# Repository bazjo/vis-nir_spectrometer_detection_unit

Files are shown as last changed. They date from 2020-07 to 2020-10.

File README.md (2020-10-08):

# vis-nir_spectrometer_detection_unit
This project contains a high-resolution detection unit for VIS/NIR spectroscopy using the Hamamatsu S1337-1010 photodiode and the Analog AD7768-1 24 Bit ADC.

It was developed as a student project in the summer term of 2020 in the course "Optical Spectroscopy and its Applications" at Cologne University of Applied Sciences.

## Getting Started

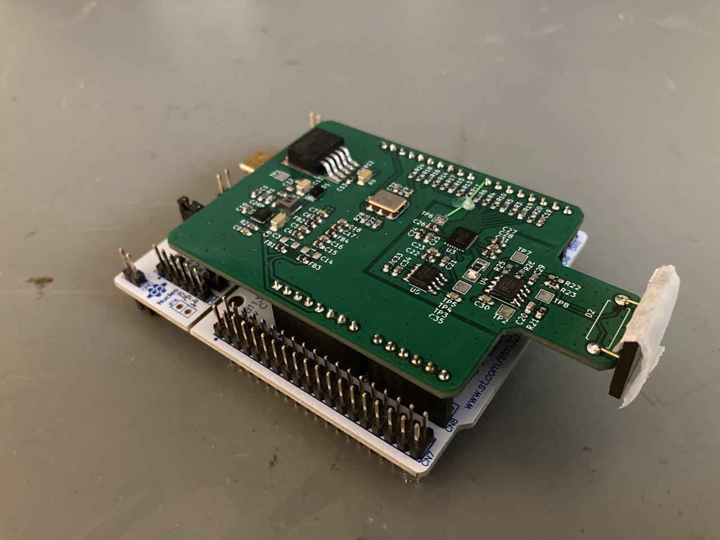
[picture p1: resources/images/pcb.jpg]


The PCB is designed to utilize an Arduino shield footprint for use with various breakout boards, such as ST Nucleo STM32 development boards or the avnet MiniZed development platform for Xilinx Zynq.

It features power filtering and an -5V inverter, the AD7768-1 DC to 204 kHz 24-Bit ADC (connected via SPI) with a 4.096 V ADR4540 and a photodiode front end featuring the AD8622 OpAmp. When a tunable clock is not available, i.e. when no FPGA is used, the main clock can be provided by an Si514 Any Frequency Programmable Oscillator (connected via I2C).

The photodiode is attached at the front to be mounted inside the spectrometer.

When assembling the PCB please look out for the bodges/errata. The PCB has been designed using kicad.

Demo applications are provided for the Arduino platform (just for the Si514 as the AD7768-1 requires 16-Bit SPI which is not yet supported by Arduino) and the STM32 platform. This application is designed for the Nucleo F401RE and was developed using the Crossley CrossWorks for ARM IDE. The code can be compiled with the trial version. This demo Application continuously sends data to a connected computer at 300 Sp/s via a serial connection.

## Theory of Operation

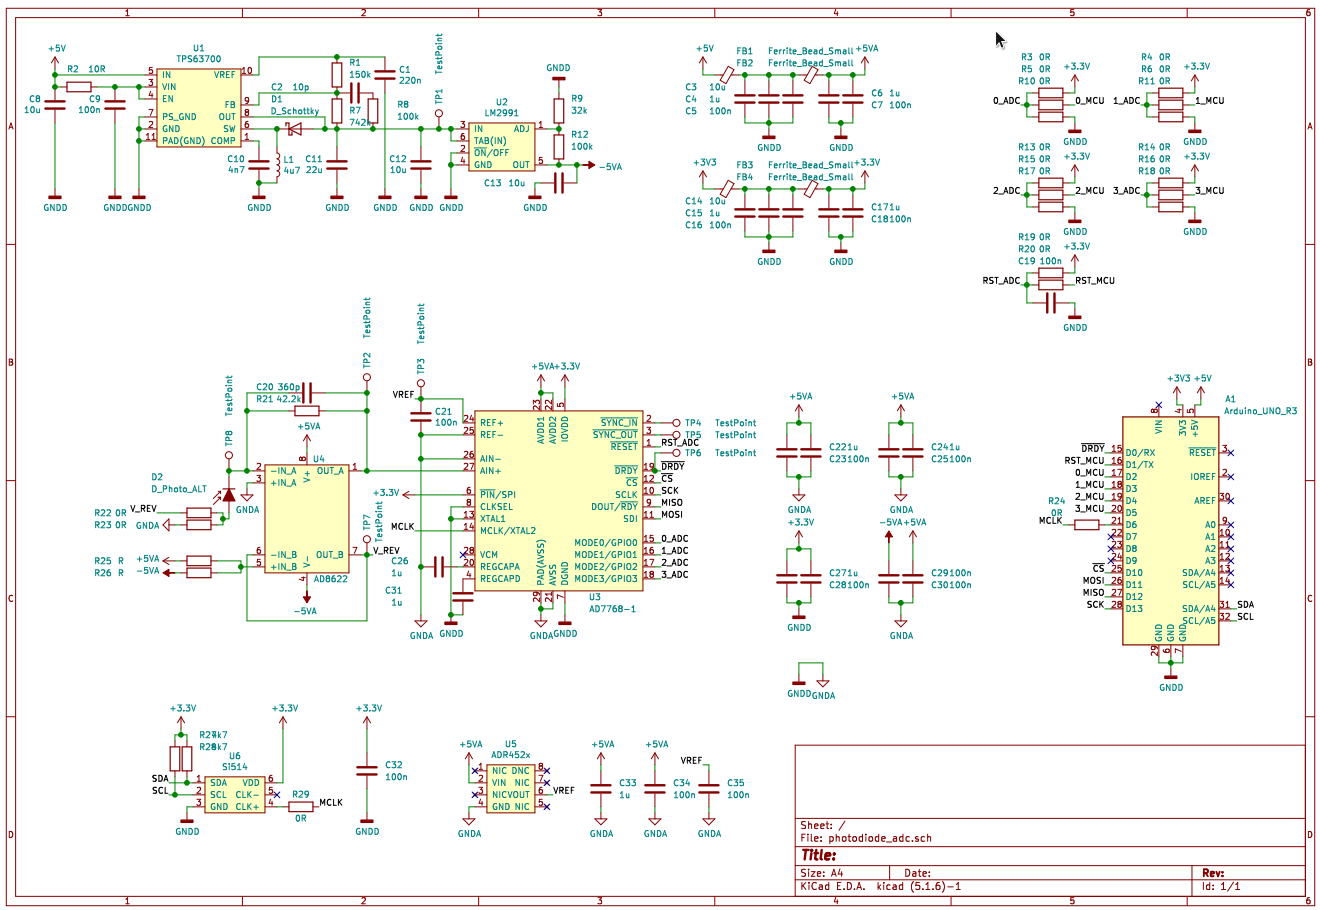
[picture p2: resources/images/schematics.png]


### Pinout
[jumpered] Pins must be connected by a designated jumper resistor.

Arduino Pin | STM32F401RE Pin | Connection
---|---|---
D0|PA3|none (!DRDY if not bodged)
D1|PA2|[jumpered] AD7768-1 !RESET
D2|PA10|[jumpered] AD7768-1 GPIO0
D3|PB3|[jumpered] AD7768-1 GPIO1
D4|PB5|[jumpered] AD7768-1 GPIO2
D5|PB4|[jumpered] AD7768-1 GPIO3
D6|PB10|[jumpered] AD7768-1 MCLK
D7|PA8|AD7768-1 !DRDY after bodge
D10|PB6|AD7768-1 !CS
D11|PA7|AD7768-1 MOSI
D12|PA6|AD7768-1 MISO
D13|PA5|AD7768-1 SCK
SDA|PB9|Si514 SDA
SCL|PB8|Si514 SCL

### Bodges/Errata
There are two problems with the pcb which are minor enough not to roll out a new revision
1. The Arduino RX/TX pins are used for GPIO. Unfortunately those Pins are used for the VCP connection on the Nucleo boards as well. The needed connection !DRDY is therefore rerouted to pin D7. This bodge can be performed by drilling the via on !DRDY with 0.8 mm drill bit and soldering a bodge wire between TP6 and D7.
2. When using the ADC on it's own, sync pulses can be generated via SPI. Those need to be send from SYNC_OUT to SYNC_IN. For this, bridge TP4 and TP5 with a 1206 0R resistor.

### PSU
The circuit uses three voltage rails. The 3V3 and 5V rails are used straight from the baseboard and are filtered through a 2-Stage LC PI-filter. The -5V rail is generated locally with TPS63700 inverter and subsequent LM2991 LDO. Power Planes are located on the second inner layer of the PCB. there are different planes for analog and digital ground, whose domains are joint below the high-speed adc interface to prevent loop currents.

### Oscillator
The Si514 Oscillator is attached via I2C and is equipped with pullup resistors. The source for the ADC MCLK can be selected between Si514 and baseboard via means of the resistor jumpers R24/R29. The tap R29 could also be used for MCLK monitoring.

### ADC + Frontend
The AD7768 was chosen for a few different reasons. First of all, it is a 24-Bit ADC suitable for low frequencies and even DC. Further, it features digital signal processing capabilities difficult to implement in a MCU. Most importantly, it allows for a wide range of decimation rates and a highly customizable sample rate so that acquisitions can be matched to the speed of a wavelength selective element. The ADC is connected via SPI. It is used in a pseudo-differential configuration with a 4.096 V reference ADR4540, to measure a voltage range between 0 an 4.096 V. The lowest possible sample rate with the highest decimation of 1024x is 300 Sp/s.

The ADC is paired with a transimpedance photodiode amplifier which is realized upon 1/2 of an AD8622 OpAmp. The values of the feedback network are matched in accordance to the photodiode sensitivity and speed. The photodiodes anode can be connected to ground via R23 or the diode can be reversed biased via R22. Reverse bias is generated through the other 1/2 of the AD8622 buffering an voltage divider R25/R26.

The photodiode is a Hamamatsu S1337-1010. It's spectral response from 190/340-1100 nm enables its use in VIS and certain NIR applications. The large area guarantees a high photosensitivity, and the rise time is fast enough for the desired spectroscopy application.

## Software Examples
The included software provides functions to interface with the hardware on the PCB.

The function `Set_Si514_Frequency()` configures the Si514 and has to be executed after every restart. It expects an array of register values which can be calculated through the Silab Utility provided in /resources/tools.

The functions to read an write from/to the AD7768-1 registers in general feature 8 bit wide addresses and values. An exemption is the result register, which is 24 bit wide an therefore is internally handled as an uint32.

After the ICs are configured, a SYNC pulse is triggered which starts the continuous adc capture. Every time a new sample is ready, a falling edge is presented to the MCU by the adc on !DRDY which is captured through an interrupt, and sets a flag, which enables a readout in the main program loop. Depending upon configuration of the variable `average_mode`, the result is either output through a serial connection right away, or after 256 samples have been averaged.

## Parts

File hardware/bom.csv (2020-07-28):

Reference | Quantity | Value | Footprint | Datasheet
A1 | 1 | Arduino_UNO_R3 | Module:Arduino_UNO_R3 | https://www.arduino.cc/en/Main/arduinoBoardUno
C1 | 1 | 220n | Capacitor_SMD:C_0603_1608Metric_Pad1.05x0.95mm_HandSolder | ~
C10 | 1 | 4n7 | Capacitor_SMD:C_0603_1608Metric_Pad1.05x0.95mm_HandSolder | ~
C11 | 1 | 22u | Capacitor_SMD:C_1206_3216Metric_Pad1.42x1.75mm_HandSolder | ~
C2 | 1 | 10p | Capacitor_SMD:C_0603_1608Metric_Pad1.05x0.95mm_HandSolder | ~
C20 | 1 | 360p | Capacitor_SMD:C_0603_1608Metric_Pad1.05x0.95mm_HandSolder | ~
C21 C19 C5 C7 C16 C18 C9 C32 C34 C35 C23 C25 C28 C29 C30 | 15 | 100n | Capacitor_SMD:C_0603_1608Metric_Pad1.05x0.95mm_HandSolder | ~
C3 C14 C8 C12 C13 | 5 | 10u | Capacitor_SMD:C_1206_3216Metric_Pad1.42x1.75mm_HandSolder | ~
C4 C6 C15 C17 C33 C26 C31 C22 C24 C27 | 10 | 1u | Capacitor_SMD:C_0603_1608Metric_Pad1.05x0.95mm_HandSolder | ~
D1 | 1 | D_Schottky | Diode_SMD:D_SMF | ~
D2 | 1 | D_Photo_ALT | Resistor_THT:R_Axial_Power_L48.0mm_W12.5mm_P7.62mm_Vertical | ~
FB1 FB2 FB3 FB4 | 4 | Ferrite_Bead_Small | Capacitor_SMD:C_0603_1608Metric_Pad1.05x0.95mm_HandSolder | ~
L1 | 1 | 4u7 | Inductor_SMD:L_Wuerth_MAPI-3020 | ~
R1 | 1 | 150k | Resistor_SMD:R_0603_1608Metric_Pad1.05x0.95mm_HandSolder | ~
R2 | 1 | 10R | Resistor_SMD:R_0603_1608Metric_Pad1.05x0.95mm_HandSolder | ~
R21 | 1 | 42.2k | Resistor_SMD:R_0603_1608Metric_Pad1.05x0.95mm_HandSolder | ~
R25 R26 | 2 | R | Resistor_SMD:R_0603_1608Metric_Pad1.05x0.95mm_HandSolder | ~
R28 R27 | 2 | 4k7 | Resistor_SMD:R_0603_1608Metric_Pad1.05x0.95mm_HandSolder | ~
R4 R6 R11 R14 R16 R18 R13 R15 R17 R3 R5 R10 R19 R20 R24 R22 R23 R29 | 18 | 0R | Resistor_SMD:R_0603_1608Metric_Pad1.05x0.95mm_HandSolder | ~
R7 | 1 | 742k | Resistor_SMD:R_0603_1608Metric_Pad1.05x0.95mm_HandSolder | ~
R8 R12 | 2 | 100k | Resistor_SMD:R_0603_1608Metric_Pad1.05x0.95mm_HandSolder | ~
R9 | 1 | 32k | Resistor_SMD:R_0603_1608Metric_Pad1.05x0.95mm_HandSolder | ~
TP4 TP5 TP6 TP2 TP3 TP7 TP1 TP8 | 8 | TestPoint | TestPoint:TestPoint_Pad_2.0x2.0mm | ~
U1 | 1 | TPS63700 | Package_SON:VSON-10-1EP_3x3mm_P0.5mm_EP1.65x2.4mm_ThermalVias
U2 | 1 | LM2991 | Package_TO_SOT_SMD:TO-263-5_TabPin6
U3 | 1 | AD7768-1 | Package_DFN_QFN:QFN-28-1EP_4x5mm_P0.5mm_EP2.65x3.65mm_ThermalVias
U4 | 1 | AD8622 | Package_SO:SOIC-8_3.9x4.9mm_P1.27mm
U5 | 1 | ADR452x | Package_SO:SOIC-8_3.9x4.9mm_P1.27mm
U6 | 1 | Si514 | Oscillator:Oscillator_SMD_IDT_JU6-6_7.0x5.0mm_P2.54mm

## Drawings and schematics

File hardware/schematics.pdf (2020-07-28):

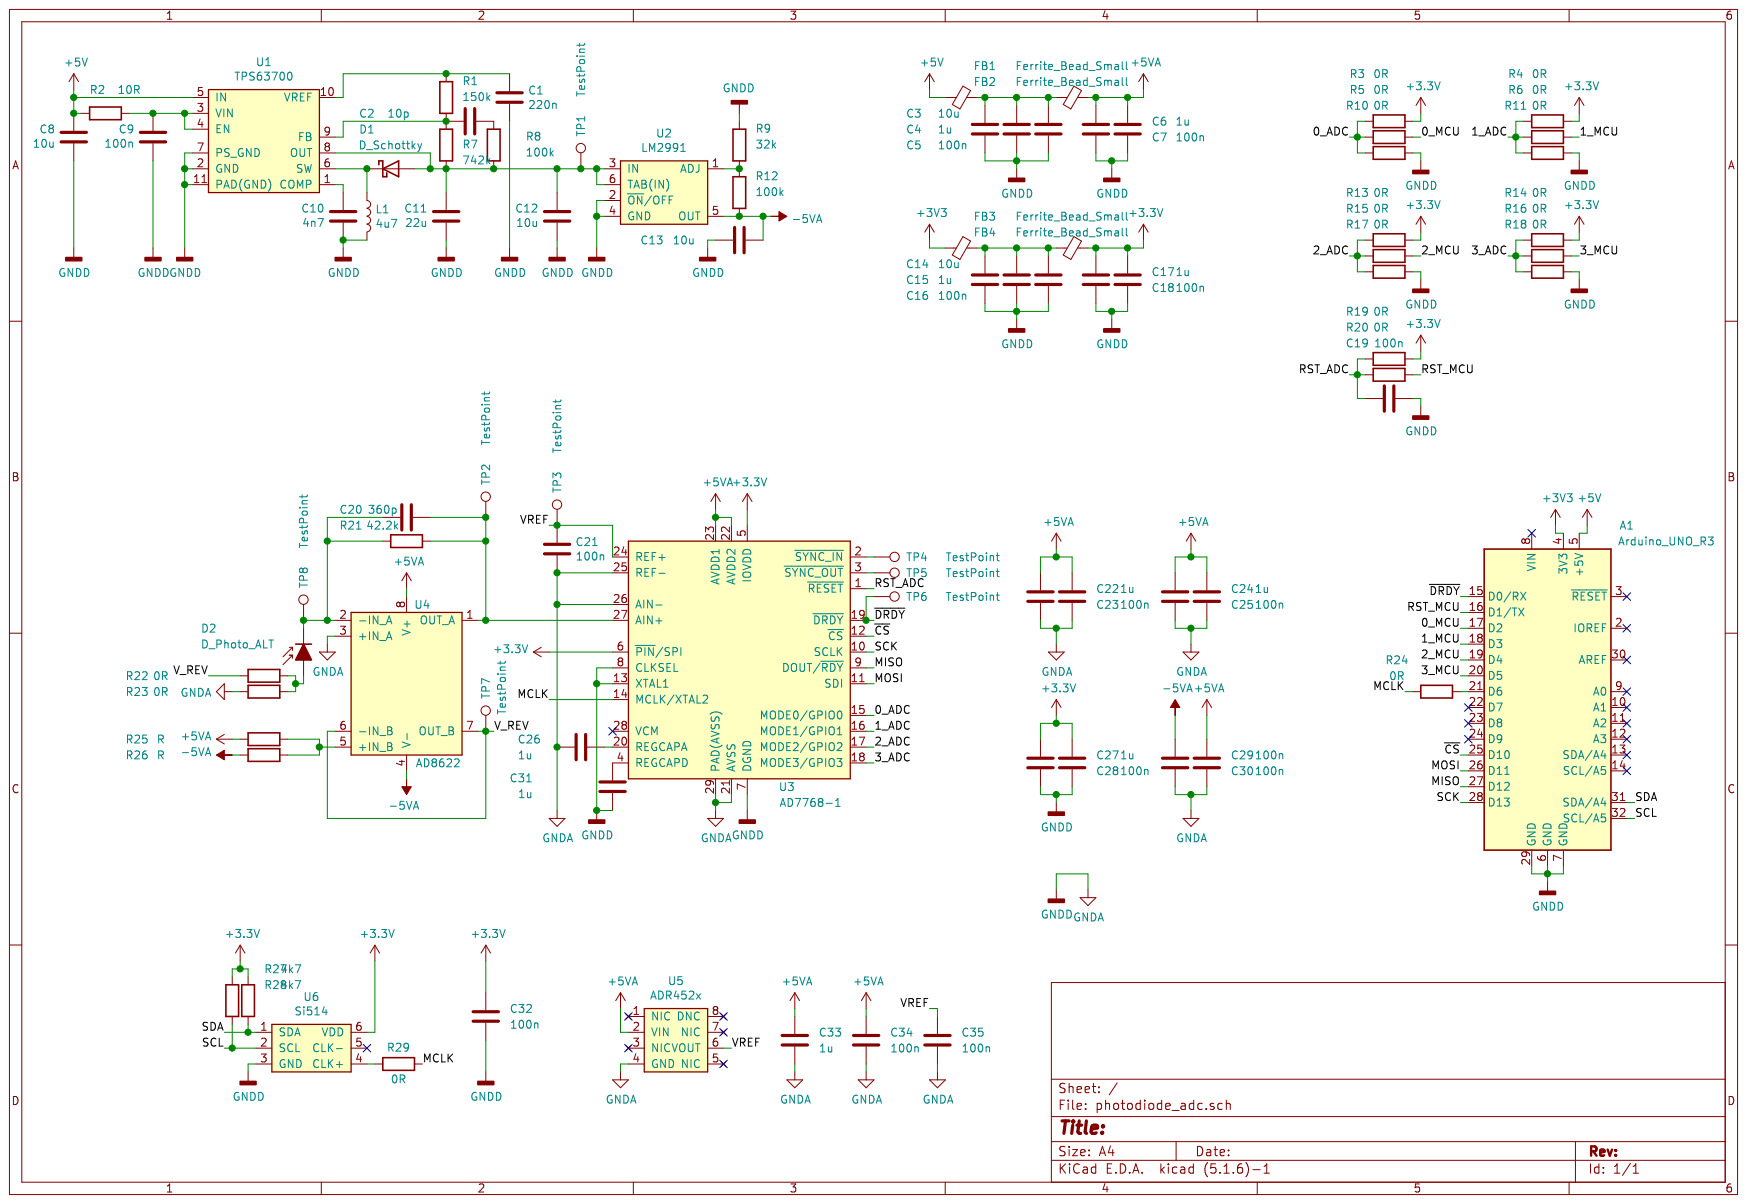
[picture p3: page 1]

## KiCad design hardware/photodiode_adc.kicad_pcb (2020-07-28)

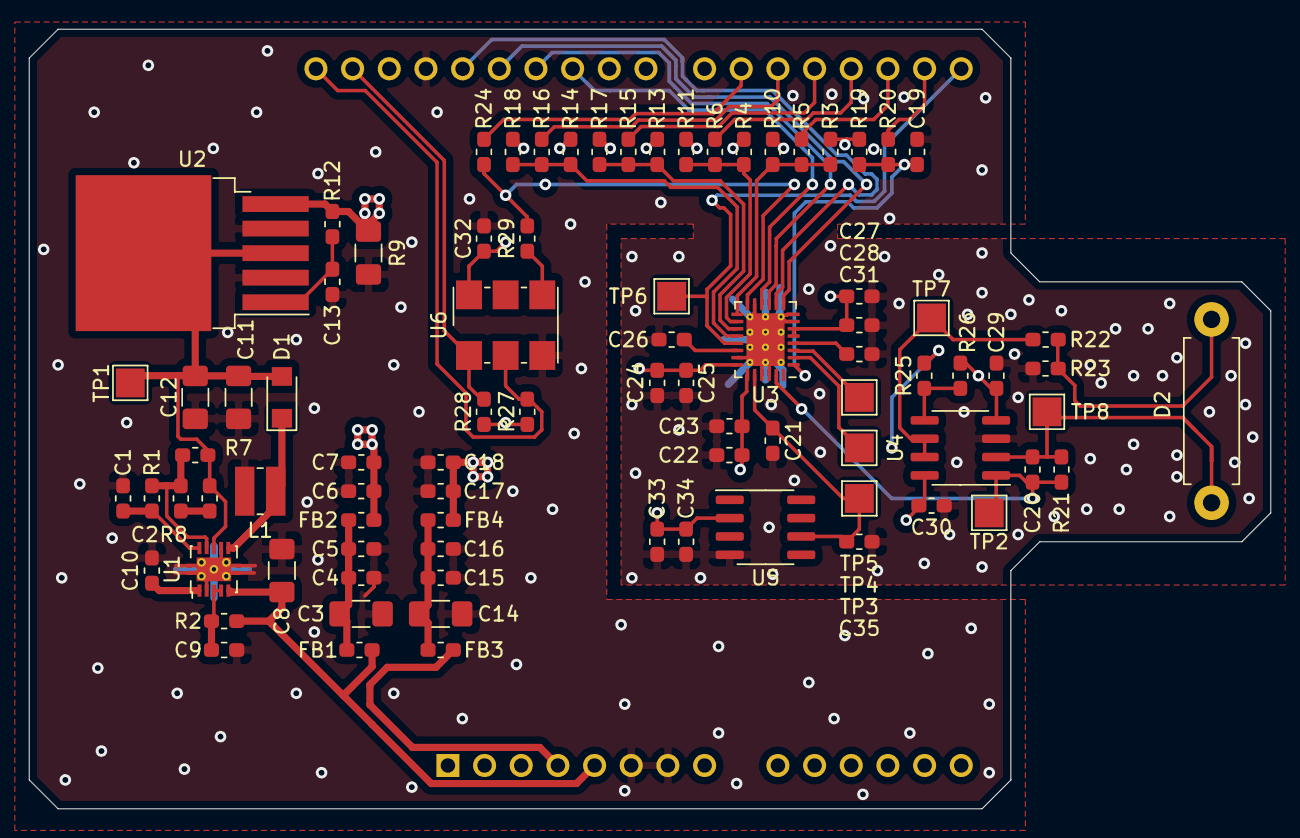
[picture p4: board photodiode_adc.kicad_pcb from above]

Board: 4 copper layers, 86.0 x 54.0 mm, 86 parts (1 on the bottom side), 45 nets.

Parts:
A1: Arduino_UNO_R3; Arduino_UNO_R3_NoSilk
C1: 220n; C_0603_1608Metric_Pad1.05x0.95mm_HandSolder
C2: 10p; C_0603_1608Metric_Pad1.05x0.95mm_HandSolder
C3, C8, C12, C13, C14: 10u; C_1206_3216Metric_Pad1.42x1.75mm_HandSolder
C4, C6, C15, C17, C22, C24, C26, C27, C31, C33: 1u; C_0603_1608Metric_Pad1.05x0.95mm_HandSolder
C5, C7, C9, C16, C18, C19, C21, C23, C25, C28, C29, C30, C32, C34, C35: 100n; C_0603_1608Metric_Pad1.05x0.95mm_HandSolder
C10: 4n7; C_0603_1608Metric_Pad1.05x0.95mm_HandSolder
C11: 22u; C_1206_3216Metric_Pad1.42x1.75mm_HandSolder
C20: 360p; C_0603_1608Metric_Pad1.05x0.95mm_HandSolder
D1: D_Schottky; D_SMF
D2: D_Photo_ALT; R_Axial_DIN0411_L9.9mm_D3.6mm_P12.70mm_Horizontal
FB1, FB2, FB3, FB4: Ferrite_Bead_Small; C_0603_1608Metric_Pad1.05x0.95mm_HandSolder
L1: 4u7; L_Wuerth_MAPI-3020
R1: 150k; R_0603_1608Metric_Pad1.05x0.95mm_HandSolder
R2: 10R; R_0603_1608Metric_Pad1.05x0.95mm_HandSolder
R3, R4, R5, R6, R10, R11, R13, R14, R15, R16, R17, R18, R19, R20, R22, R23, R24, R29: 0R; R_0603_1608Metric_Pad1.05x0.95mm_HandSolder
R7: 742k; R_0603_1608Metric_Pad1.05x0.95mm_HandSolder
R8, R12: 100k; R_0603_1608Metric_Pad1.05x0.95mm_HandSolder
R9: 32k; R_0603_1608Metric_Pad1.05x0.95mm_HandSolder
R21: 42.2k; R_0603_1608Metric_Pad1.05x0.95mm_HandSolder
R25, R26: R; R_0603_1608Metric_Pad1.05x0.95mm_HandSolder
R27, R28: 4k7; R_0603_1608Metric_Pad1.05x0.95mm_HandSolder
TP1, TP2, TP3, TP4, TP5, TP6, TP7, TP8: TestPoint; TestPoint_Pad_2.0x2.0mm
U1: TPS63700; VSON-10-1EP_3x3mm_P0.5mm_EP1.65x2.4mm_ThermalVias
U2: LM2991; TO-263-5_TabPin6
U3: AD7768-1; QFN-28-1EP_4x5mm_P0.5mm_EP2.65x3.65mm_ThermalVias
U4: AD8622; SOIC-8_3.9x4.9mm_P1.27mm
U5: ADR452x; SOIC-8_3.9x4.9mm_P1.27mm
U6: Si514; Oscillator_SMD_IDT_JU6-6_7.0x5.0mm_P2.54mm

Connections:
+3V3: A1.4, C17.1, C18.1, C27.1, C28.1, C32.1, FB3.2, FB4.1, R3.1, R4.1, R13.1, R14.1, R19.1, R27.1, R28.1, U3.5, U3.6, U6.6
+5V: A1.5, C8.2, FB1.2, R2.2, U1.5
+5VA: C6.1, C7.1, C22.1, C23.1, C24.1, C25.1, C30.1, C33.1, C34.1, FB2.1, R25.2, U3.22, U3.23, U4.8, U5.2
-5VA: C13.2, C29.1, R12.1, R26.2, U2.5, U4.4
/0_ADC: R3.2, R5.2, R10.2, U3.15
/0_MCU: A1.17, R5.1
/1_ADC: R4.2, R6.2, R11.2, U3.16
/1_MCU: A1.18, R6.1
/2_ADC: R13.2, R15.2, R17.2, U3.17
/2_MCU: A1.19, R15.1
/3_ADC: R14.2, R16.2, R18.2, U3.18
/3_MCU: A1.20, R16.1
/MCLK: R24.2, R29.2, U3.14
/MISO: A1.27, U3.9
/MOSI: A1.26, U3.11
/RST_ADC: C19.2, R19.2, R20.2, U3.1
/RST_MCU: A1.16, R20.1
/SCK: A1.28, U3.10
/SCL: A1.32, R27.2, U6.2
/SDA: A1.31, R28.2, U6.1
/VREF: C21.1, C35.1, TP3.1, U3.24, U5.6
/V_REV: R22.2, TP7.1, U4.6, U4.7
/~CS~: A1.25, U3.12
/~DRDY~: A1.15, TP6.1, U3.19
GNDA: A1.6, A1.7, A1.29, C1.2, C3.2, C4.2, C5.2, C6.2, C7.2, C8.1, C9.1, C10.1, C11.1, C12.1, C13.1, C14.2, C15.2, C16.2, C17.2, C18.2, C19.1, C21.2, C22.2, C23.2, C24.2, C25.2, C26.2, C27.2, C28.2, C29.2, C30.2, C31.1, C32.2, C33.2, C34.2, C35.2, L1.2, R9.2, R10.1, R11.1, R17.1, R18.1, R23.2, U1.2, U1.7, U1.11, U2.2, U2.4, U3.7, U3.8, U3.13, U3.21, U3.25, U3.26, U3.29, U4.3, U5.4, U6.3
unnamed: A1.21, R24.1
unnamed: C1.1, R1.2, U1.10
unnamed: C2.1, R8.2
unnamed: C2.2, R1.1, R7.2, U1.9
unnamed: C3.1, C4.1, C5.1, FB1.1, FB2.2
unnamed: C9.2, R2.1, U1.3, U1.4
unnamed: C10.2, U1.1
unnamed: C11.2, C12.2, D1.2, R7.1, R8.1, TP1.1, U1.8, U2.3, U2.6
unnamed: C14.1, C15.1, C16.1, FB3.1, FB4.2
unnamed: C20.1, R21.1, TP2.1, U3.27, U4.1
unnamed: C20.2, D2.1, R21.2, TP8.1, U4.2
unnamed: C26.1, U3.20
unnamed: C31.2, U3.4
unnamed: D1.1, L1.1, U1.6
unnamed: D2.2, R22.1, R23.1
unnamed: R9.1, R12.2, U2.1
unnamed: R25.1, R26.1, U4.5
unnamed: R29.1, U6.4
unnamed: TP4.1, U3.2
unnamed: TP5.1, U3.3

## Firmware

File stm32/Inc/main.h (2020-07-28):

/* USER CODE BEGIN Header */
/**
  ******************************************************************************
  * @file           : main.h
  * @brief          : Header for main.c file.
  *                   This file contains the common defines of the application.
  ******************************************************************************
  ** This notice applies to any and all portions of this file
  * that are not between comment pairs USER CODE BEGIN and
  * USER CODE END. Other portions of this file, whether 
  * inserted by the user or by software development tools
  * are owned by their respective copyright owners.
  *
  * COPYRIGHT(c) 2020 STMicroelectronics
  *
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
  ******************************************************************************
  */
/* USER CODE END Header */

/* Define to prevent recursive inclusion -------------------------------------*/
#ifndef __MAIN_H
#define __MAIN_H

#ifdef __cplusplus
extern "C" {
#endif

/* Includes ------------------------------------------------------------------*/
#include "stm32f4xx_hal.h"

/* Private includes ----------------------------------------------------------*/
/* USER CODE BEGIN Includes */

/* USER CODE END Includes */

/* Exported types ------------------------------------------------------------*/
/* USER CODE BEGIN ET */

/* USER CODE END ET */

/* Exported constants --------------------------------------------------------*/
/* USER CODE BEGIN EC */

/* USER CODE END EC */

/* Exported macro ------------------------------------------------------------*/
/* USER CODE BEGIN EM */

/* USER CODE END EM */

/* Exported functions prototypes ---------------------------------------------*/
void Error_Handler(void);

/* USER CODE BEGIN EFP */

/* USER CODE END EFP */

/* Private defines -----------------------------------------------------------*/
#define B1_Pin GPIO_PIN_13
#define B1_GPIO_Port GPIOC
#define USART_TX_Pin GPIO_PIN_2
#define USART_TX_GPIO_Port GPIOA
#define USART_RX_Pin GPIO_PIN_3
#define USART_RX_GPIO_Port GPIOA
#define MCLK_Pin GPIO_PIN_10
#define MCLK_GPIO_Port GPIOB
#define MODE0_Pin GPIO_PIN_10
#define MODE0_GPIO_Port GPIOA
#define TMS_Pin GPIO_PIN_13
#define TMS_GPIO_Port GPIOA
#define TCK_Pin GPIO_PIN_14
#define TCK_GPIO_Port GPIOA
#define MODE1_Pin GPIO_PIN_3
#define MODE1_GPIO_Port GPIOB
#define MODE3_Pin GPIO_PIN_4
#define MODE3_GPIO_Port GPIOB
#define MODE2_Pin GPIO_PIN_5
#define MODE2_GPIO_Port GPIOB
#define CS_Pin GPIO_PIN_6
#define CS_GPIO_Port GPIOB
/* USER CODE BEGIN Private defines */

/* USER CODE END Private defines */

#ifdef __cplusplus
}
#endif

#endif /* __MAIN_H */

/************************ (C) COPYRIGHT STMicroelectronics *****END OF FILE****/

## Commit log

2020-07-28 add kicad project files for rev 0.1
    [bom.csv, photodiode_adc.kicad_pcb, photodiode_adc.sch, phtodiode_adc-B_Cu.gbr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]
2020-07-28 add register calc utility for si514, add arduino demo for si514
2020-09-22 implement i2c and spi prototype for stm32
2020-10-08 remove arduino prototype
